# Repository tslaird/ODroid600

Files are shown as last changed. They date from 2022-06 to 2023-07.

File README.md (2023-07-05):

# ODroid600

The motivation behind this tool came from the inconvenience of having
to obtain repeated bacterial growth curve measurements coupled with the fact that the spectrophotometer in my graduate research lab was broken and I needed to make measurements. I happened to realize that Pyrex 9820 glass test tubes (25 mm outer diameter) fit well inside schedule 40 PVC piping (). Thus my goal was to use a scaffold of PVC with low-cost electronic components to create an automated spectrophotometer. Additionally, so called "inexpensive" devices that were being marketed were still in the price range of several thousand dollars and thus still inaccessible to low-budget laboratories.

## Components
|Component| Quantity | Combined Price |  Link |
| --------|----|----|-------|
| 3/4 inch PVC pipe | 3 | $16.17 | https://www.acehardware.com/departments/plumbing/pipe/plastic-pipe/4361424 |
| 3/4 inch PVC T coupler | 6 | $10.14 | https://www.acehardware.com/departments/plumbing/pipe-fittings/plastic-fittings/43137
| 3/4 inch PVC elbow coupler | 4 | $3.16 | https://www.acehardware.com/departments/plumbing/pipe-fittings/plastic-fittings/43123 |
| Flanged nylon bushing (Hillman Group #58071 [0.312 O.D.])| 4 | $10.99 (40 pack) | https://www.amazon.com/B00MNDPO26 |
| Arduino UNO REV3 | 1 | $28.50 | https://www.amazon.com/dp/B008GRTSV6 |
| Breadboard | 1 | $9.99 | https://www.amazon.com/dp/B07LFD4LT6 |
| Assorted resistors | 1 kit | $11.99 | https://www.amazon.com/dp/B072BL2VX1 |
| Jumper wires | $7.99 | 1 pack | https://www.amazon.com/dp/B07GD2BWPY |
| Orange LEDs (602-610 nm) | 4 | $6.99 (for 100) |  https://www.amazon.com//dp/B077XD7MVB |
| Used P1000 tip box | 1 | Free |  NA |

Total Cost: $105.92

*Notes:*
* Some of the above components are sold in large quantities and can be used to make more than one ODroid600.
* Some of the component prices may vary depending on date accessed.
* Some costs can be reduced for example by using competitor brands to Arduino.

Tools needed:
PVC cutter or hacksaw
Drill with 1/4 inch drill bit

## Assembling base
1) Cut the following lengths and quantities of PVC for each frame component:
side pieces: x inches (2 total), x inches (2 total)
rear piece: x inches
tube stalk connectors: x inches (2 total), x inches (2 total), x inches (2 total)
2) Assemble the base according to the diagram below. The pieces should fit snugly together without the need for any glue or adhesive.
However, once the design is finalized you can glue the PVC frame if desired.

Diagram coming soon!

## Assembling tube stalks
1) Cut PVC pipe to 4.75 inches
2) Place the cut stalk in a PVC T and mark holes to drill 0.375 inches (~1cm) from the junction between the T and tubing (Tip: Use the centering line on the T to make sure drill hole markings are aligned on either side of the pipe)
3) Remove the cut stalk from the PVC T and carefully drill the marked holes ensuring as best as possible to have the two holes aligned. If needed, file away excess PVC debris from the drilled holes.
Use 1/4 inch drill bit to drill holes on either side.
4) Place the ACE adapters in each of the drilled holes so that the bottom edge aligns with the inner diameter of the PVC pipe
5) Place the holding stalk within a T of the base
6) Repeat for the 3 other test-tube holding stalks
7) Ensure that the ACE adapters are at the same height above the T adapter in each holding stalk

## Comparison with GENESYS 50 spectrophotometer

First a bacterial suspension of *Pseudomonas putida* 1290 made in a plastic cuvette to 1.0 OD using the Genesys 50 spectrophotometer. The bacterial suspension was serially diluted 2-fold a total of 10 times in 50 mL Falcon tubes. A Pyrex 9820 test tube was placed inside each of the ODroid600 holders as well as in the test tube holding attachment for the Genesys 50 spectrophotometer. Then the serially diluted samples were successively dispensed and moved from each sensor to obtain a reading (1 channel in the Genesys 50 spectrophotometer and 4 channels in the ODroid600). Sample absorbance was read successively from the most diluted sample to the least diluted (i.e. the original bacterial suspension). All tubes were left inside their respective holding chambers (tube stalks of the ODroid600 or the test tube holding attachment for the Genesys 50 spectrophotometer) in order to minimize errors or confounding factors that occur from repositioning the test tubes in the different instruments. The only thing that changed in the experiment was the solution inside the test tubes. The analog phototransistor readings from each channel of the Arduino on the ODroid600 were obtained using the serial monitor within the Arduino IDE software. The phototransistor values from the sample dilutions were transformed to optical density using the following formula: -log10(sample_value/blank_value).

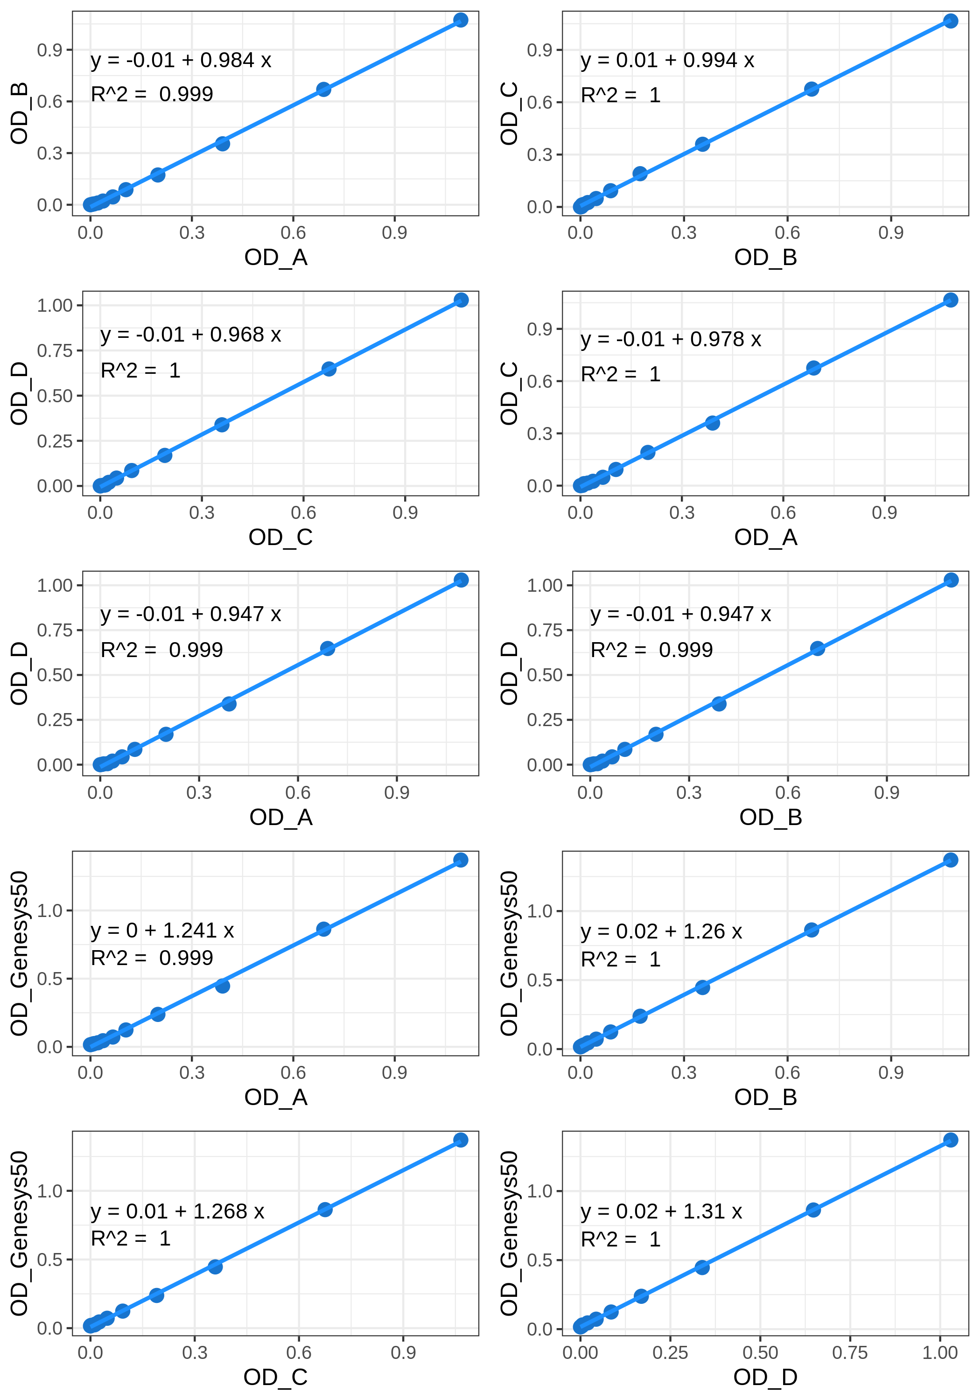
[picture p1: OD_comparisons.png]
ODroid600 comparisons between channels and with GENESYS 50 spectrophotometer


**ODroid600 comparisons between channels and with GENESYS 50 spectrophotometer**

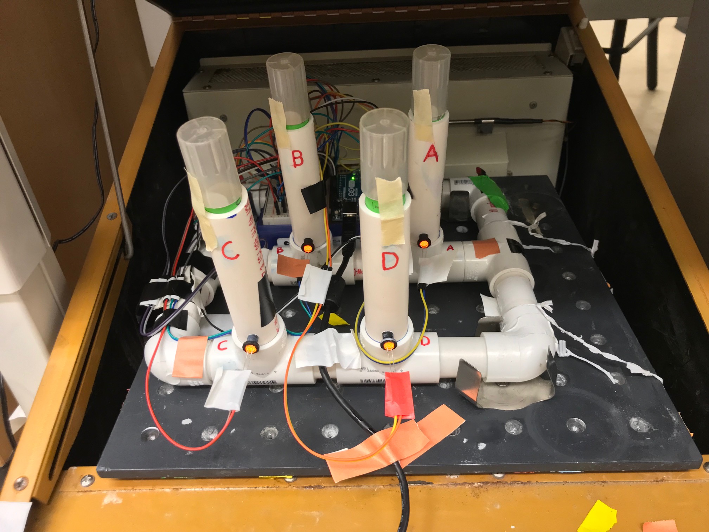
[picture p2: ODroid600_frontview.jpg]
Image of ODroid600 set up in a shaking incubator

**Image of ODroid600 set up in a shaking incubator**

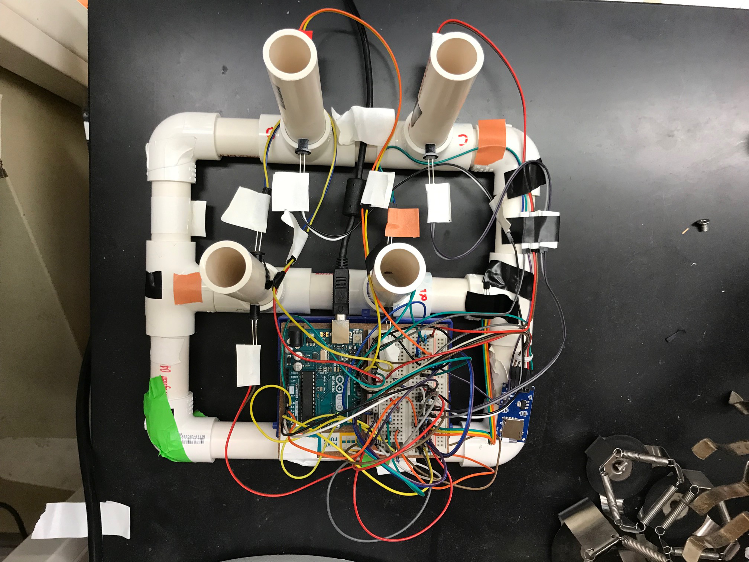
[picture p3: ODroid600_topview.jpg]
Aerial view of ODroid600

**Aerial view of ODroid600**

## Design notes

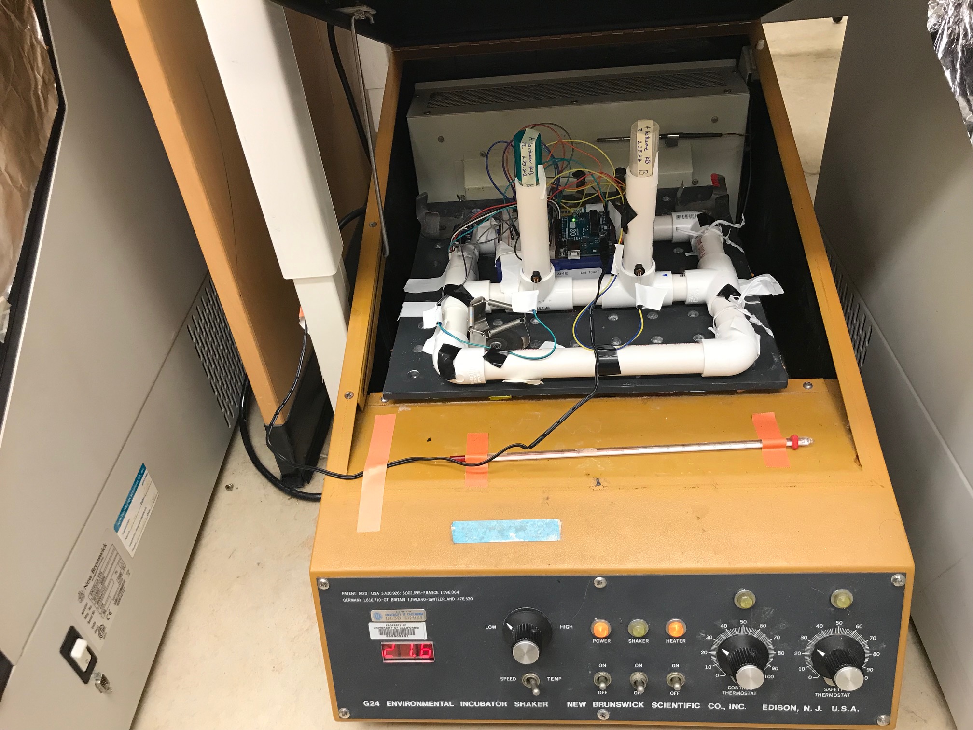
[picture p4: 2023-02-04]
ODroid600_2channels.jpg

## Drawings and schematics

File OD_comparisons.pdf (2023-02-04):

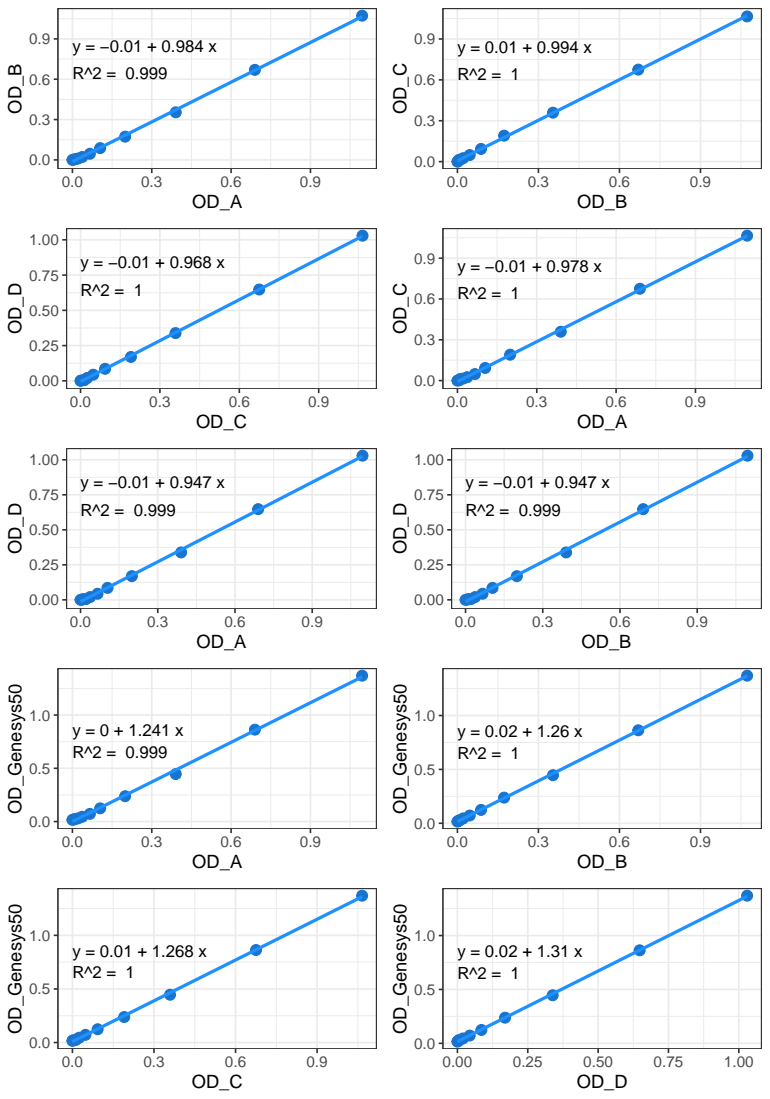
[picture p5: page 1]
OD_Genesys50

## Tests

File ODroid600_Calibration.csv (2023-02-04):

Tube_id | Concentration | Dilution | Genesys50 | A | B | C | D
Blank | 0 | NA | 0.016 | 573 | 603 | 535 | 471
10 | 0.001953125 | 9 | 0.02 | 565 | 599 | 533 | 469
9 | 0.00390625 | 8 | 0.024 | 559 | 596 | 521 | 466
8 | 0.0078125 | 7 | 0.03 | 545 | 589 | 517 | 465
7 | 0.015625 | 6 | 0.045 | 526 | 574 | 505 | 450
6 | 0.03125 | 5 | 0.072 | 492 | 543 | 479 | 426
5 | 0.0625 | 4 | 0.124 | 450 | 493 | 432 | 387
4 | 0.125 | 3 | 0.238 | 362 | 405 | 345 | 319
3 | 0.25 | 2 | 0.446 | 233 | 267 | 234 | 216
2 | 0.5 | 1 | 0.863 | 117 | 129 | 113 | 106
1 | 1 | 0 | 1.37 | 46 | 51 | 46 | 44

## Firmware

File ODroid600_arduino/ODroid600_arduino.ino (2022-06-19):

#include <SPI.h>
#include <SD.h>
long pt_A = A0;
long pt_B = A2;
long pt_C = A3;
long pt_D = A4;
long readingA = 0;
long readingB = 0;
long readingC = 0;
long readingD = 0;
int tempSens = A1;
int tempInput;
double temp;
File myFile;

void setup() {
  // put your setup code here, to run once:
pinMode(2, OUTPUT);
pinMode(3, OUTPUT);
pinMode(6, OUTPUT);
pinMode(7, OUTPUT);
pinMode(pt_A, INPUT); 
pinMode(pt_B, INPUT); 
pinMode(pt_C, INPUT); 
pinMode(pt_D, INPUT); 
Serial.begin(9600);
Serial.print("Initializing SD card...");
if (!SD.begin(4)) {
Serial.println("initialization failed!");
while (1);
}
Serial.println("initialization done.");
myFile = SD.open("log.txt", FILE_WRITE);
if (myFile) {
    Serial.print("Writing header to file...\n");
    myFile.println("minutes,transistor_value_A,transistor_value_B,transistor_value_C,transistor_value_D,temperature");
    // close the file:
    myFile.close();
    Serial.println("done writing header");
  } else {
    // if the file didn't open, print an error:
    Serial.println("error opening file");
  }

}

void loop() {
  // put your main code here, to run repeatedly:
digitalWrite(2,HIGH);
digitalWrite(3,HIGH);
digitalWrite(6,HIGH);
digitalWrite(7,HIGH);
delay(10);
long readingA_mean = 0;
long readingB_mean = 0;
long readingC_mean = 0;
long readingD_mean = 0;
for (int i=0; i < 100; i++) {
readingA_mean = readingA_mean + long(analogRead(pt_A));
readingB_mean = readingB_mean + long(analogRead(pt_B));
readingC_mean = readingC_mean + long(analogRead(pt_C));
readingD_mean = readingD_mean + long(analogRead(pt_D));
delay(100);
}
digitalWrite(2, LOW);
digitalWrite(3, LOW);
digitalWrite(6, LOW);
digitalWrite(7, LOW);
tempInput = analogRead(A1); //read the temperature
temp = (double)tempInput / 1024; //find percentage of input reading
temp = temp * 5; //multiply by 5V to get voltage
temp = temp - 0.5; //Subtract the offset
temp = temp * 100; //Convert to degrees
readingA_mean = readingA_mean/long(100);
readingB_mean = readingB_mean/long(100);
readingC_mean = readingC_mean/long(100);
readingD_mean = readingD_mean/long(100);
Serial.println(readingA_mean);
Serial.println(String(millis()*1.66667e-5)+','+ String(readingA_mean)+','+String(readingB_mean)+','+String(readingC_mean)+','+String(readingD_mean)+','+String(temp));
myFile = SD.open("log.txt", FILE_WRITE);
myFile.println(String(millis()*1.66667e-5)+','+ String(readingA_mean)+','+String(readingB_mean)+','+String(readingC_mean)+','+String(readingD_mean)+','+String(temp));
myFile.close();
delay(60000); // take a reading every 60 seconds

}

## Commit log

2022-06-19 created repo with working arduino code
2022-07-15 started fritz diagram
    [ODroid600_friting_diagram.fzz]
2022-07-15 edited fritz
    [ODroid600_friting_diagram.fzz]
2023-02-04 added data and analysis script
    [ODroid600_Calibration.csv]
